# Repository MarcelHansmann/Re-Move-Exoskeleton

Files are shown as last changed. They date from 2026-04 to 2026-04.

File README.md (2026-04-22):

# Re-Move: Open-Source Knee Exoskeleton

<p align="center">
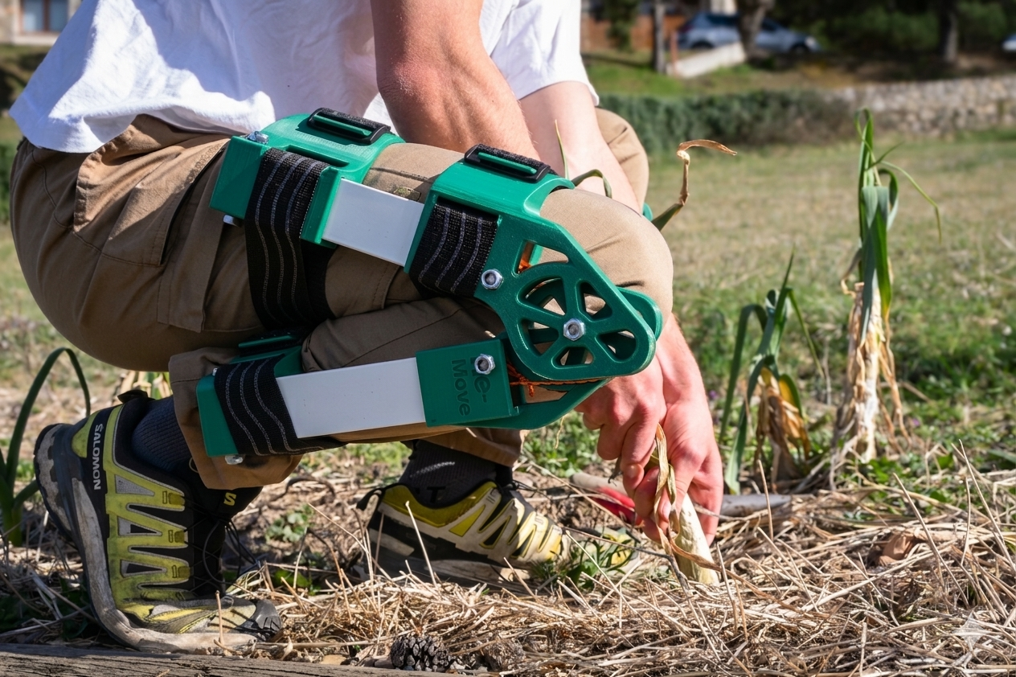
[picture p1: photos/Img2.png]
  
</p>

*Designed to democratize access to mobility assistance.*

## Overview
Re-Move is a knee exoskeleton designed to assist with squatting movements. Rooted in an open-source philosophy and engineered for user fabrication, its goal is to democratize access to mobility assistance. Current commercial solutions cost around €2,000; **Re-Move reduces this cost to just €50 per unit**, making it forty times more affordable.

The system stores potential energy in elastic springs during knee flexion (the downward phase) and releases it in a controlled manner during extension (the upward phase), providing a **23% assistance** to the user's effort. Structurally, the device consists of four 3D-printed elements assembled with standardized metal components that provide all necessary structural rigidity.

<p align="center">
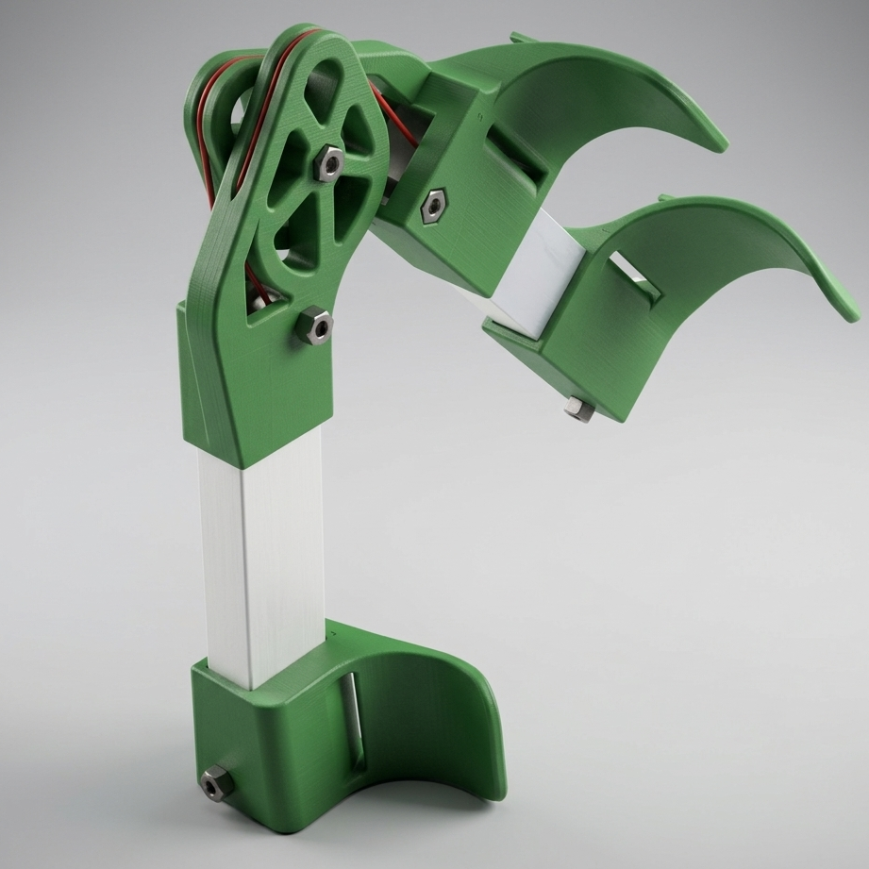
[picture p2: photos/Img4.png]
  
</p>

---

## Bill of Materials (BOM) & Files

The total cost of materials is approximately €50. You will need both the standard hardware components and the 3D printed parts.

### 1. Standard Hardware (Off-the-shelf)

| Component | Quantity | Notes | Where to Buy / Link |
| :--- | :---: | :--- | :--- |
| **Aluminum Profile** (45x25mm) | 2 meters | Structural chassis | [Buy at Leroy Merlin](https://www.leroymerlin.es/productos/perfil-forma-rectangular-de-aluminio-blanco-standers-alt-45-x-an-25mm-x-l-2-m-87477282.html) |
| **Extension Springs** (18x115mm) | 4 units | Energy storage (Max 8kg load) | [Buy at Leroy Merlin](https://www.leroymerlin.es/productos/muelle-tensor-de-acero-cincado-standers-carga-max-8-kg-18x115mm-91007856.html) |
| **Velcro Straps** | 4 units | User attachment | [Buy at Amazon](https://www.amazon.es/dp/B0B18BQSF3/) |
| **Polyester Cord** | 1 unit | Mechanism linkage (50m roll) | [Buy at Leroy Merlin](https://www.leroymerlin.es/productos/cuerda-de-poliester-de-50-m-y-19-75-kg-de-carga-util-16746884.html) |
| **M8 Threaded Rod** | 1 meter | For rigidity | Any local hardware store |
| **M8 Hex Nuts** | 10 units | Assembly fasteners | Any local hardware store |

---

### 2. 3D Printed Parts & Print Settings

**Print with Bambu Studio (Plug & Play):**

Download the `.3mf` plates with all elements ready to go — settings are already configured inside the files, just slice and print!

 📥 **[Download Right Leg .3mf File](https://github.com/MarcelHansmann/Re-Move-Exoskeleton/raw/main/BambuLabFiles/RightLegPlate.3mf)**

 📥 **[Download Left Leg .3mf File](https://github.com/MarcelHansmann/Re-Move-Exoskeleton/raw/main/BambuLabFiles/LeftLegPlate.3mf)**

*Basic Slicing Guidelines:*
- **Material:** PLA Basic recommended.
- **Walls/Perimeters:** Minimum 2 walls.
- **Infill:** 15% general infill.
- **Modifier Infill:** 45% infill in the areas defined by the modifier files.
- **Supports:** Activate supports.

---

### 3. CAD Source Files (SolidWorks)

For those who want to modify or inspect the design, the original SolidWorks files are available below.

*Right Leg (4 parts):*
- 📥 [Download Right Leg Part 1.SLDPRT](https://github.com/MarcelHansmann/Re-Move-Exoskeleton/raw/main/cad/Part1_Right.SLDPRT)
- 📥 [Download Right Leg Part 2.SLDPRT](https://github.com/MarcelHansmann/Re-Move-Exoskeleton/raw/main/cad/Part2_Right.SLDPRT)
- 📥 [Download Right Leg Part 3.SLDPRT](https://github.com/MarcelHansmann/Re-Move-Exoskeleton/raw/main/cad/Part3_Right.SLDPRT)
- 📥 [Download Right Leg Part 4.SLDPRT](https://github.com/MarcelHansmann/Re-Move-Exoskeleton/raw/main/cad/Part4_Right.SLDPRT)

*Left Leg (4 parts):*
- 📥 [Download Left Leg Part 1.SLDPRT](https://github.com/MarcelHansmann/Re-Move-Exoskeleton/raw/main/cad/Part1_Left.SLDPRT)
- 📥 [Download Left Leg Part 2.SLDPRT](https://github.com/MarcelHansmann/Re-Move-Exoskeleton/raw/main/cad/Part2_Left.SLDPRT)
- 📥 [Download Left Leg Part 3.SLDPRT](https://github.com/MarcelHansmann/Re-Move-Exoskeleton/raw/main/cad/Part3_Left.SLDPRT)
- 📥 [Download Left Leg Part 4.SLDPRT](https://github.com/MarcelHansmann/Re-Move-Exoskeleton/raw/main/cad/Part4_left.SLDPRT)

*Shared Part (both legs):*
- 📥 [Download Shared Part.SLDPRT](https://github.com/MarcelHansmann/Re-Move-Exoskeleton/raw/main/cad/Part5_Shared.SLDPRT)

---

## 🛠️ Assembly Instructions
Re-Move is designed for easy self-assembly. You do not need advanced technical skills, and the process takes less than 2 hours.

We have created a highly visual, step-by-step assembly manual to guide you through cutting the aluminum, placing the springs, and routing the straps.

📖 📥 **[Download the Visual Assembly Manual (PDF)](https://github.com/MarcelHansmann/Re-Move-Exoskeleton/blob/main/Assembly%20Manual%20Re-Move.pdf)**

---

## ⚠️ Safety Disclaimer
**Please read carefully before building or using.**
Re-Move is an experimental, open-source engineering project. **It is NOT a certified medical device.** It is designed solely to assist with the vertical squatting motion, not for walking or supporting full body weight in cases of severe paralysis.

Be careful while using the tools to modify the aluminium profile. They tend to be dumb-proof, but are still designed to make their way through harder things than your fingers.

The author has no medical knowledge (so far) and assumes no responsibility for injuries. Use at your own risk.

---

## Contributing
Contributions are welcome! If you improve the design, find a bug, 
or want to adapt it for a different use case, feel free to open 
an Issue or submit a Pull Request.

---

## 📄 License
Re-Move: Open-Source Knee Exoskeleton © 2025 by Marcel Hansmann is licensed under [CC BY-NC-SA 4.0](https://creativecommons.org/licenses/by-nc-sa/4.0/).

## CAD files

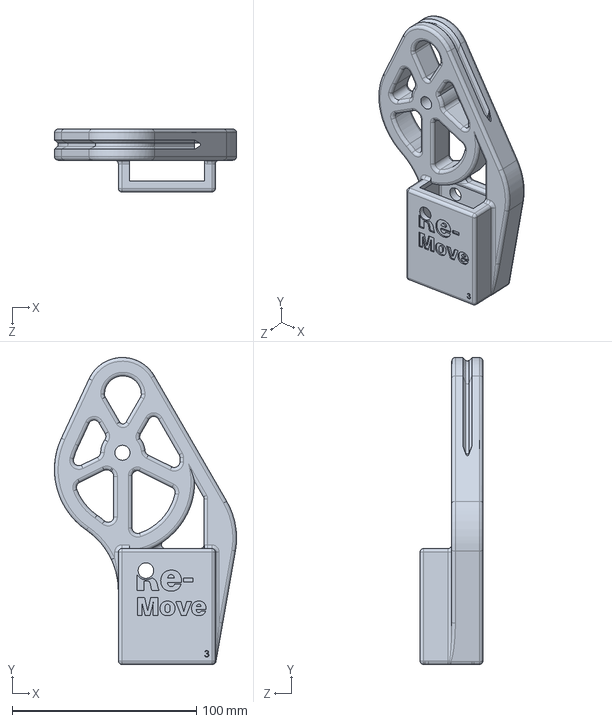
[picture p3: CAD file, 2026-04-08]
cad/Part3_Right.SLDPRT
98.9 x 166.7 x 34.2 mm

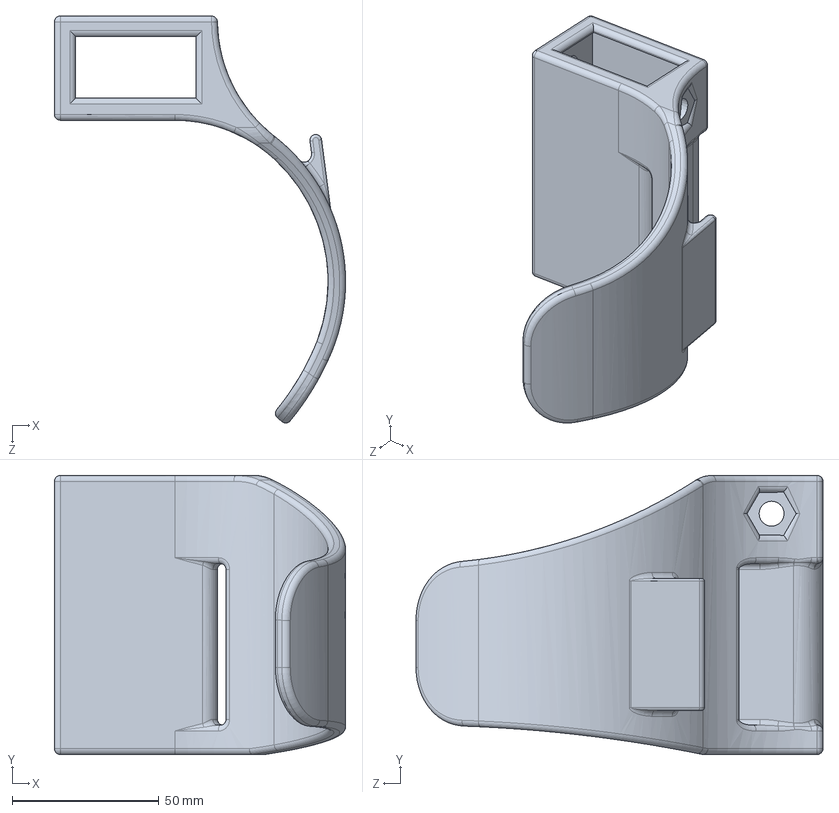
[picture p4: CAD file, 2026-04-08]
cad/Part1_Left.SLDPRT
99.1 x 95.0 x 138.6 mm

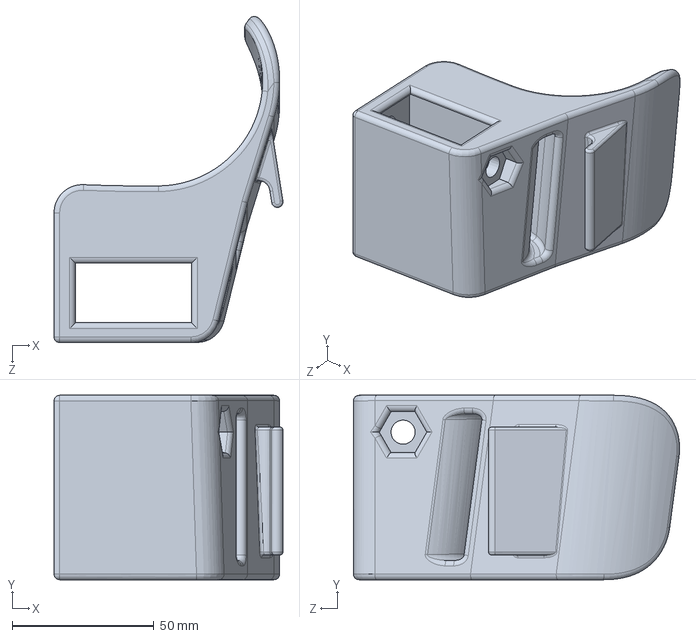
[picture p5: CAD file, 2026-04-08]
cad/Part4_Right.SLDPRT
80.7 x 65.0 x 114.9 mm

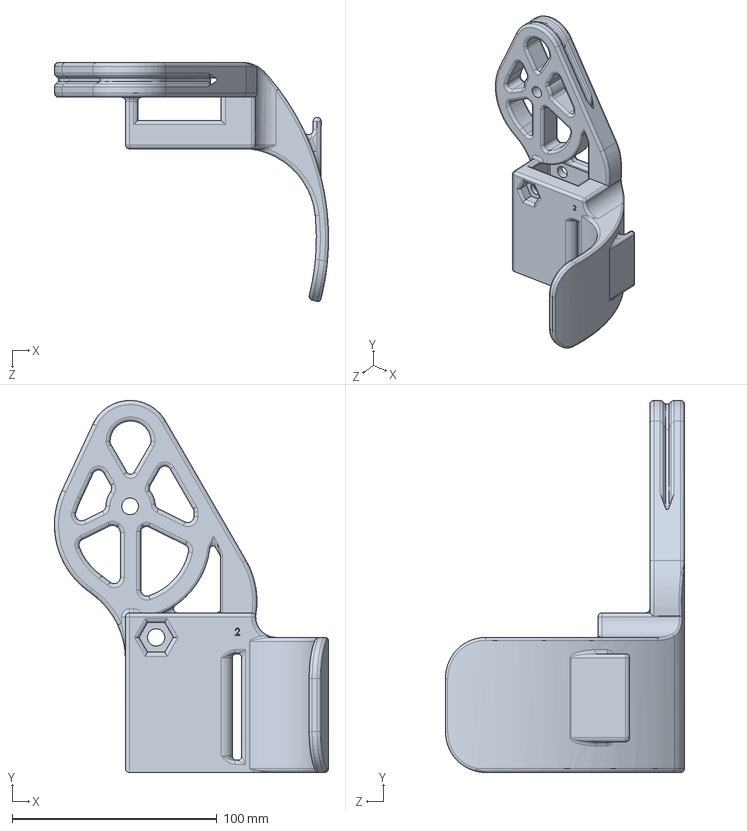
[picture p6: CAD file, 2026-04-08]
cad/Part2_Right.SLDPRT
133.9 x 181.7 x 116.8 mm

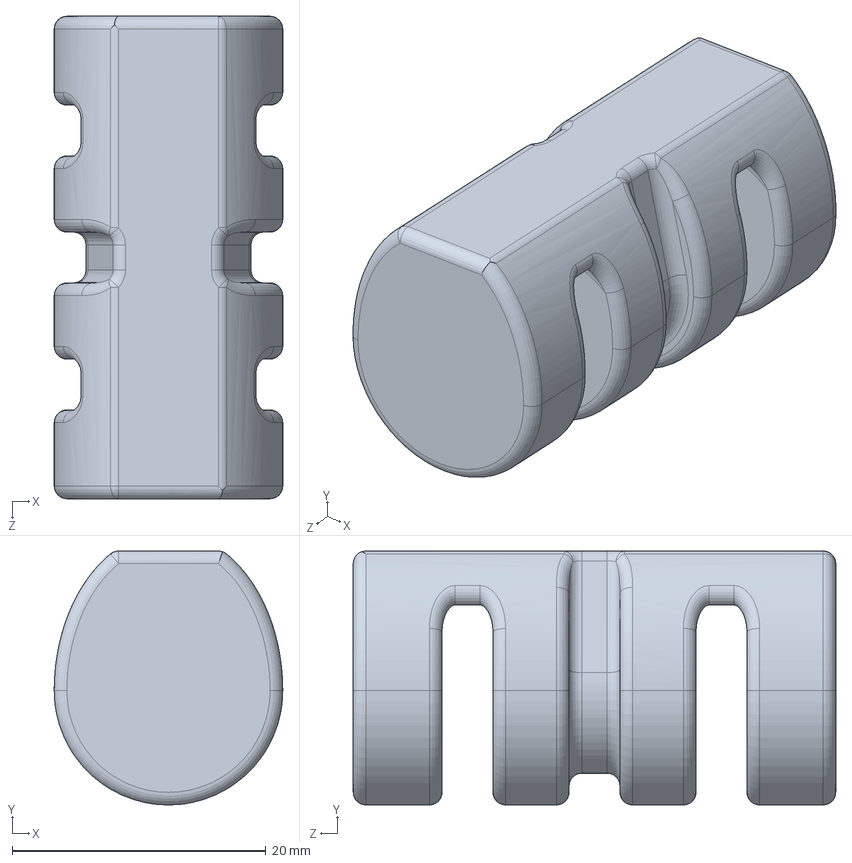
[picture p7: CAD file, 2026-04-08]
cad/Part5_Shared.SLDPRT
18.0 x 20.0 x 38.0 mm

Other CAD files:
cad/Part4_left.SLDPRT
cad/Part1_Right.SLDPRT
cad/Part2_Left.SLDPRT
cad/Part3_Left.SLDPRT

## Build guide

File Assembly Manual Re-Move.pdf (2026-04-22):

# Assembly Manual

# Howto

# Re-Move

1

# 3DPrinter-BambuLab

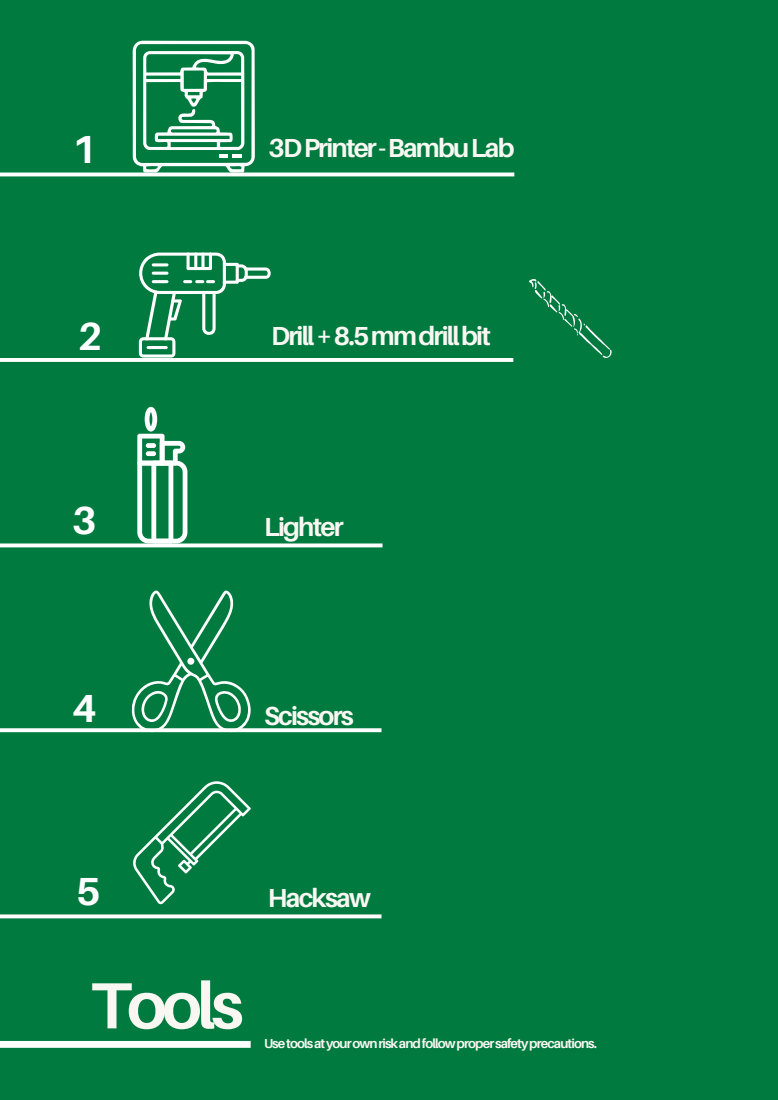
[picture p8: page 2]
Tools; Drill+8.5mmdrillbit; Lighter; Scissors; Hacksaw; Usetoolsatyourownriskandfollowpropersafetyprecautions.

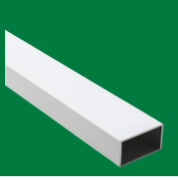
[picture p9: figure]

2

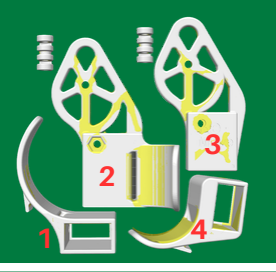
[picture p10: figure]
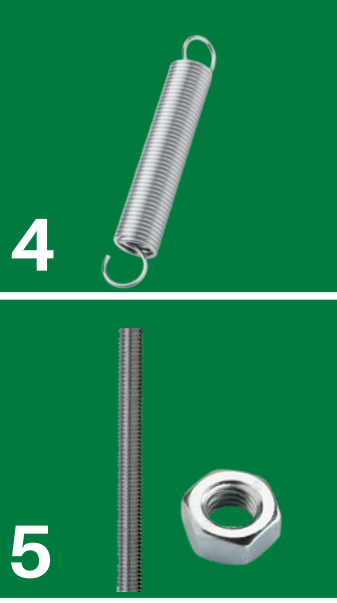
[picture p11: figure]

# Parts

1 1

3

6

# 3DPrinted

Downloadtheplate(rightorleftleg)andprintitusingaBambuLab3Dprinter.

Ifyoudon’townaBambuLabprinter,youcanprintitatyourlocalFabLab: https://www.fablabs.io/

Cut2pieces(235mmeach)usingahacksaw.

Cut 2pieces,about400mm each.Thenmelt theendswithalightertopreventfraying

M8bar:cutwiththehacksaw
2x55mm
2x35mm
1x30mm

# 25x45mm aluminiumprofile

# Rope

# Springsx4

# M8: bar+10nuts

# VelcroStraps

Thepiecesarenumberedforabetterassembly

FilesandlinksforpartsareavailableinGitHub: https://github.com/MarcelHansmann/Re-Move-Exoskeleton

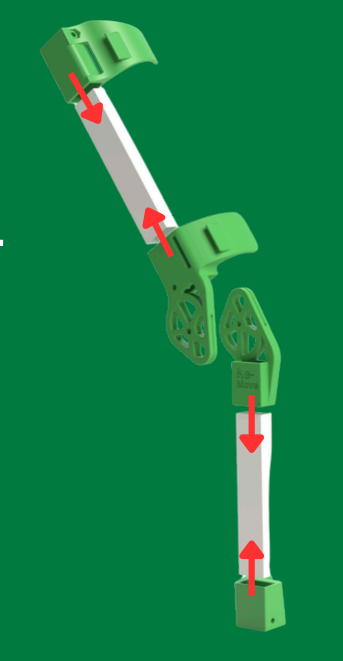
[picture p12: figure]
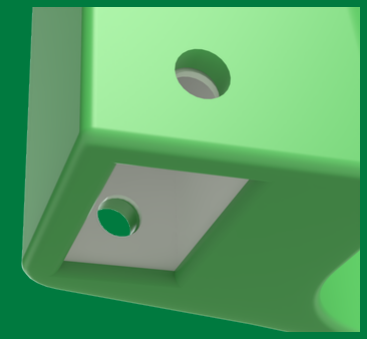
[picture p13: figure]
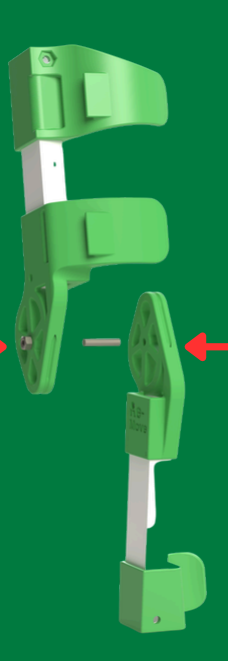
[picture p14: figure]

# Structuralassembly

# Assemblepieces1,2,3and4with aluminiumbars

8holesintotal,4foreachbar

# Drilla8.5mmholeinthealuminiumprofiles Usetheholesinthe3D-printedpartasaguide

# Jointhetwoparts

# Step1

UseM8barsize30mmand2nuts

# Step2

# Step3

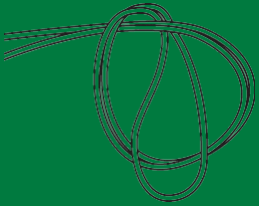
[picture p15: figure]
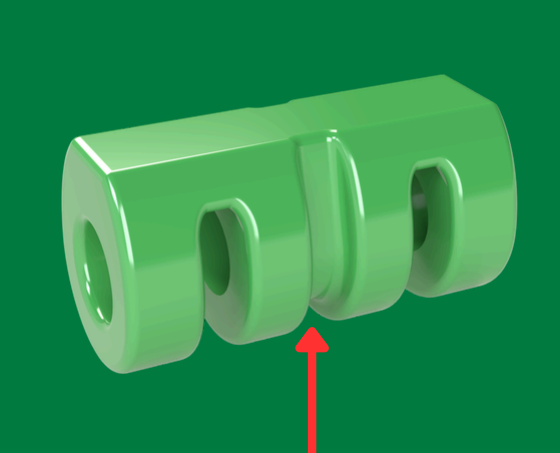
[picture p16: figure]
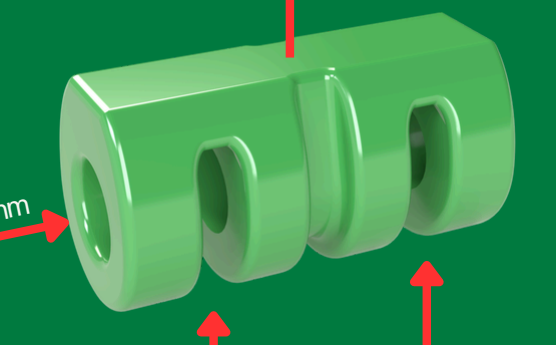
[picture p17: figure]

# Mechanismassembly

# Tieanoverhandloopattheendofeachropeand attachittothecenterofeachspringunifier

# Assembleeachsetof2springswith thespringunifiers

# Repeattheprocesswiththesecondspringunifier

1xM8barL30mm
2xSpring

1xRope400mm
1x3DPrintedSpringunifier

1.Spring

2.Spring

3. M8barL30mm

ro

pe

Followthecorrectorder,asshownintheimage

# Step1

# Step2

# Step3

# Assemble the spring sub-assembly insidethealuminiumprofiles

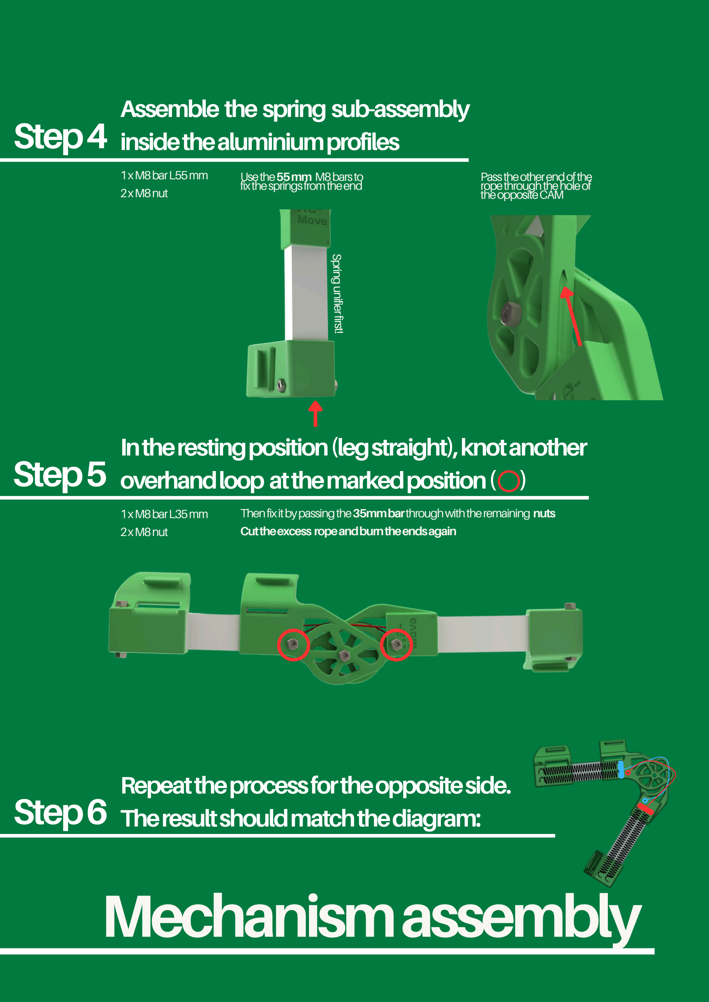
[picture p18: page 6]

# Intherestingposition(legstraight),knotanother overhandloop atthemarkedposition( )

Thenfixitbypassingthe35mmbarthroughwiththeremaining nuts Cuttheexcess ropeandburntheendsagain

# Mechanismassembly

1xM8barL55mm
2xM8nut

1xM8barL35mm
2xM8nut

Usethe55mm M8barsto
fixthespringsfromtheend

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
Passtheotherendofthe
ropethroughtheholeof
theoppositeCAM

Repeattheprocessfortheoppositeside.

# Theresultshouldmatchthediagram:

# Step4

# Step5

# Step6

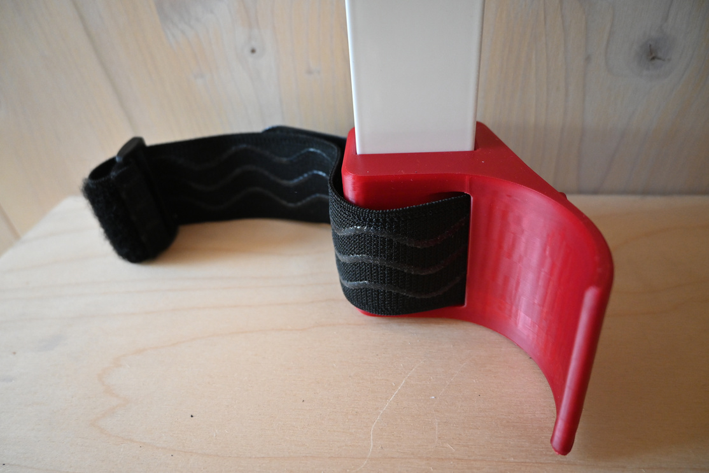
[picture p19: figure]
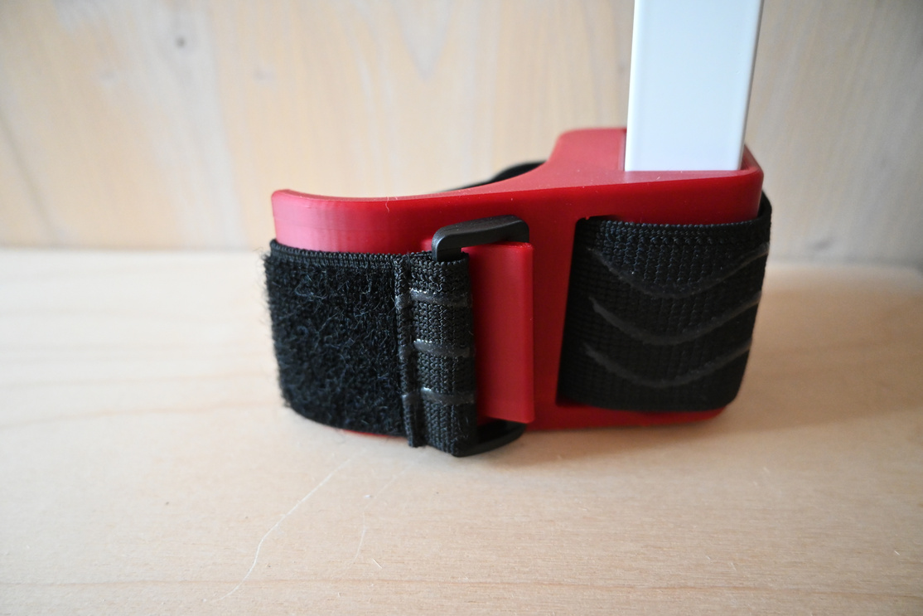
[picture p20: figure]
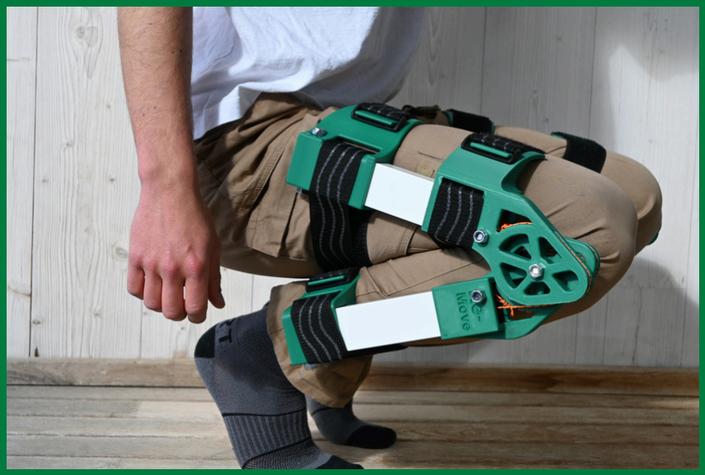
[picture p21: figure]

# Attachtoyourleg

# Addthe Velcrostrapstoeachpart

# Attachtoyourleg

3x Velcrostraps | PasstheVelcrostrapthroughthehole,withtheVelcrosidefacingthe3D-printedmaterial. Theresultshouldbeasshownintheimagesbelow Repeattheprocessforall3oftheparts

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

Warning!

Thisdeviceisfor
experimentalpurposes
onlyandisnot
medicallycertified.

# Step1

# Step2
